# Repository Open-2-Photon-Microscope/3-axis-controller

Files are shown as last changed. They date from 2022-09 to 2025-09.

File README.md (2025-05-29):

# 3-axis-controller

A manipulator device to operate microscope stage XYZ translations. This project was specifically designed for the OpenFlexure Delta Stage.
  
## Assembly

### Assembling the Board
1. Order the (2 layer) board from a PCB manufacturer (e.g. JLCPCB) by uploading [this file](electronics/integrated_board/Fabrication%20files/integrated_board_gerbers.zip).
1. Using the [BOM](BOM.xlsx), solder together the integrated board from [electronics/integrated_board](electronics/integrated_board). The board is labeled with the locations and values of resistors, capacitors etc.
    * _Make sure to solder socket headers to the board and slot in the esp32 and pcf8575 modules rather than soldering them directly to the board. Sometimes things go wrong and they will be very hard to remove..._
    * _All parts are intended to be soldered as sitting on the top face of the board - any differences seen in the 3D view of the PCB in KiCAD should be ignored_

## Software
### Setting up MicroPython with Thonny IDE
1. Follow the tutorial on [this page](https://randomnerdtutorials.com/getting-started-thonny-micropython-python-ide-esp32-esp8266/) if you haven't already done so when assembling the board.   
### Upload the Code
1. Download the code [here](micropython/)
1. Open them all in Thonny.
    * *Connect your board to your PC via micro USB.*
1. In Thonny, in the files panel (`view > files`) navigate to the location of the code to be installed
1. Highlight all files and folders, including `lib`
1. Right click and select `Upload to /`
1. __CHECK:__ Does the file layout in the esp32 look like that on this GitHub?  

### Assembling the controller
1. Assemble the JST-XH cables mentioned in the BOM
1. For each button and flip switch, cut one crimped wire in half and solder before attaching to the JST-XH head Orientation doesn't matter.  
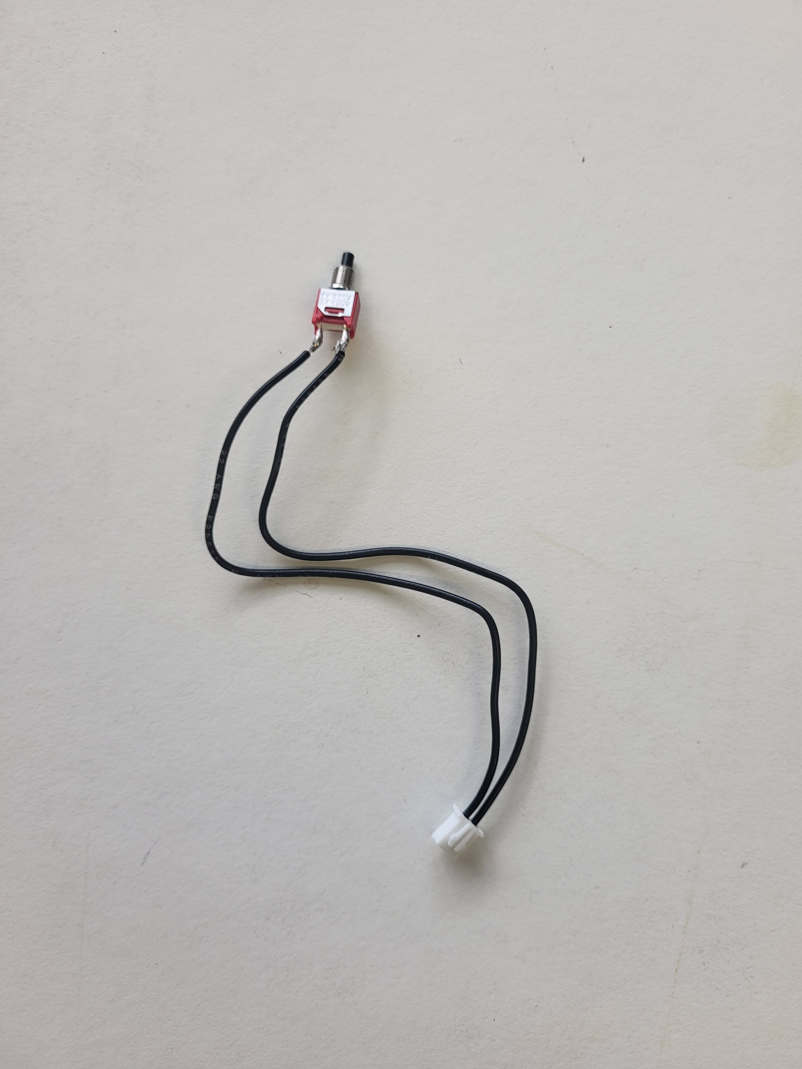
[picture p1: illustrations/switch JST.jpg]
All switches in the panel use one crimped cable cut in half
    
1. Print the [enclosure top](box%20design/enclosure_top.stl) and assemble as shown. Include the other rotary encoders and switches (not shown). The appropriate washers and nuts to screw onto the front face should be shipped with each component. Use M3x10 screws for the LCD.
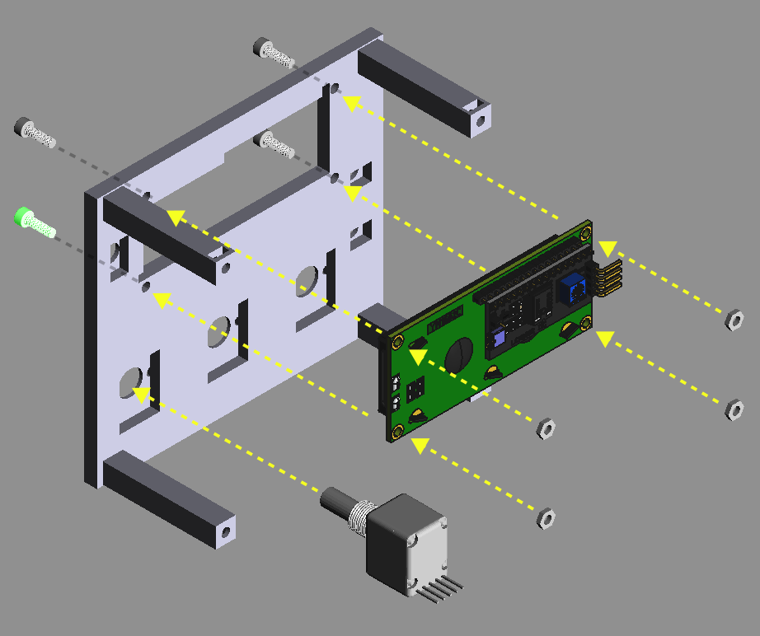
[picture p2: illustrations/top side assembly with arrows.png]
Assemble the top of the controller
      
1. Use a 4-pin JST cable to connect the LCD to the marked port. **Make sure** the GND and VCC pins are attached to the same connection on the main and LCD board.
    * _NOTE: there is a variable resistor on the back of the LCD board that adjusts the contrast, so don't screw the whole box shut until you've tested the text appears correctly_  
1. Use a 5-pin JST cable for each rotary encoder. **MAKE SURE** the GND pin connects to the pin marked with "-" on the encoder.
1. Plug in all the switches to the board to their closest port.
    * __DO NOT PLUG SWITCHES INTO THE PORTS MARKED AS 12V/GND AS IT MAY START A FIRE AND SOME FEATURES MAY NOT WORK AS INTENDED__  
1. Once you are confident the LCD is displaying text correctly when powered on, assemble the [enclosure](box%20design/enclosure.stl) as shown. Make sure to print the [feet](box%20design/enclosure_feet.stl) in some TPU for grip. Use M3x16 (or longer).  
 * _Note you should have all components wired up and screwed in at this point, not all of this is shown on the diagram._

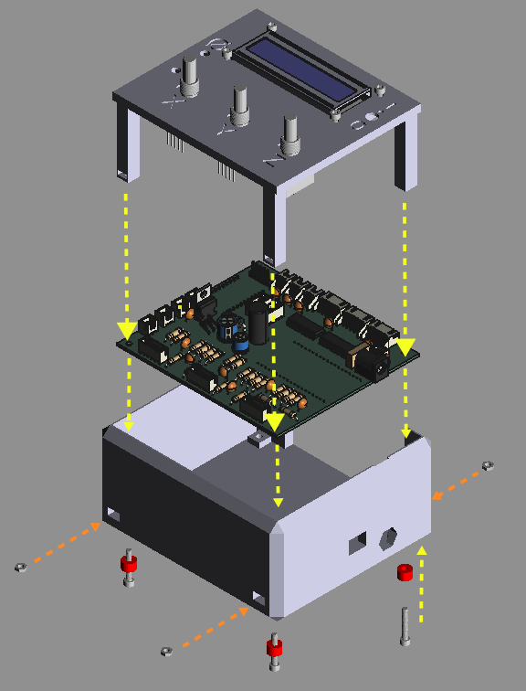
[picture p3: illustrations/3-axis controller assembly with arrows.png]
Assemble the whole box!
    
    
### Connecting to the Delta Stage
1. Split the length (2M) of ribbon cable at the ends into 3 strips of 5 wires, and 3 strips of 2 wires. You can peel away the remaining wires and discard them.
    * _Note it may be helpful for cable management not to entirely separate the 3x5 and 3x2 strips._
1. Crimp **one** end of the cable, and slot into JST XH 5 or 2 cable headers respectively.
1. Put a short length of heat-shrink tubing on each remaining end of **all** wires.
1. Next, solder the remaining 3x5 wires to straight JST HX 5 pin headers (male)
    * _Ensure the orientation of both ends of the cable is such that each lane could form a complete loop if it were plugged into itself without any twist. (i.e. each in and out pin is the same)_
1. Solder the sets of 2 wires to the footswitches - one to the middle-pin, the other to the pin towards the hinge of the lever.
    * _Ensure this configuration is such that a circuit is made (not broken) when the switch is pressed_
1. Use hot air or a soldering iron to shrink the heat-shrink tubing and cover these solder joints.
1. Use m2x8 screws to attach the switches to the [modified feet of the Delta Stage](https://github.com/Open-2-Photon-Microscope/OF-larger-delta-stage/blob/main/3D_designs/STL/feet_with_endstop.stl) and use these in place of the ones on the official models when [assembling the actuators](https://build.openflexure.org/openflexure-delta-stage/v1.2.2/pages/index_transmission/pages/assembling_the_actuators.html)
    * Make sure to use the modified models found [here](https://github.com/Open-2-Photon-Microscope/OF-larger-delta-stage/tree/main/3D_designs/STL) for the open 2-photon project  

### Installing the I2C library
#### You may need to install the `lib` portion of the I2C code another way - the above method __should__ work, so only follow these instructions if something is not behaving as expected.
1. Download [micropython-i2c-lcd-0.1.1.tar.gz](https://pypi.org/project/micropython-i2c-lcd/#files)
1. In Thonny go to `Tools > Manage Packages`
    * _make sure the esp32 is still plugged in to your computer_
1. Click the __Install from local file__ link and select the `.tar.gz` file you downloaded
1. __CHECK:__ Does the file layout in the esp32 look like that on this GitHub? You should not need to but you may have to rename the folder to ensure all the code is looking in the right place...

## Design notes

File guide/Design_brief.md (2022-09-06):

# Design brief

|Function|Constraint|Level|
| ------------- | ------------- | ------------- |
| Connect rotary encoders | Present an user interface | present rotary encoder shafts/rods : 9,8 mm holes | 
|  |  | countersink the nuts : nut thickness of 3 mm, fastening thickness 8 mm | 
|  |  | split the interface into three rotary encoders, rotary encoders dimensions : 15,9 x 21,3 mm |
|  | Contain rotary encoders and wires | rotary encoder thickness 18,5 mm |
|  |  | 35 mm depth for wires |
| Rotary encoder driver boards | Contain and fix the 3 PCBs | mounting holes center distance : 40 x 27 mm | 
|  |  | mounting holes 3,5 for M3 screws |
|  |  | board dimensions : 52 x 39 mm |
| BeeHive board | Contain and fix the Beehive board | mounting holes center distance : 76 x 67 | 
|  |  | mounting holes 3,5 for M3 screws |
|  |  | board dimensions : 85 x 76 |
|  | Power the board | Hole for 12V power supply cable and micro usb cable : 20 x 20 |
| ULN driver boards | Contain and fix the 3 PCBs | mounting holes center distance : 30,5 x 26 | 
|  | | mounting holes diameter M3 |
|  | | board dimensions : 35 x 31 |
|  | Command the motors | Hole(s) for the IN cables : 35 x 6 |

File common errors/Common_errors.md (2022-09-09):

# Common errors

## 1.  Builder

### a.  BeeHive / esp32

- Don’t power the BeeHive board with the micro usb cable only. Always use simultaneously the 12 V power supply and the 5 V micro usb power supply.
- Don’t use the analog pins called “A1”, “A2” and “A3”.
- Don’t use the pins 0 and 4 when you are connected to the computer via usb connection.

### b.  Electrical connections

If you notice that a circuit isn’t working, although each electrical connection was double checked, try to remove and solder its components to the board again.

## 2.  User

### a.  Running the code

- If the error “pin can only be input” appears, make sure that rotary encoders and motors aren’t connected to any analog pin. The analog pins are located in the “A1”, “A2” and “A3” BeeHive connectors. 



- If you’re having trouble connecting the esp32, try to close the jupyter notebook and the command prompt and start all over again.
If it persists, you can erase and flash again the esp32. 



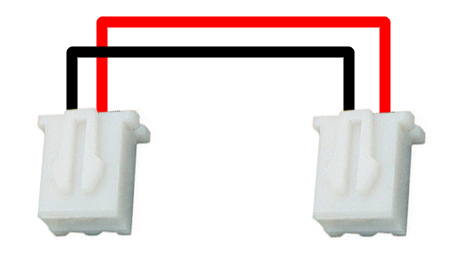
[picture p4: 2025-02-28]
illustrations/jst connect.png

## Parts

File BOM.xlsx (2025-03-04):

3-axis Controller BOM
Designator* | Name | Part Name | ppu | Qty | Cost | URL
 | I2C LCD 16x2 |  | 3.33 | 1 |  | https://www.amazon.co.uk/AZDelivery-HD44780-Display-Characters-Arduino/dp/B07JH6GHPR
Can replace? | Rotary Encoders | ENA1J-B28 L100L | 45.96 | 3 |  | https://uk.rs-online.com/web/p/motion-control-sensors/6928623?gb=s
 | Power Supply 12V |  | 8.33 | 1 |  | https://uk.rs-online.com/web/p/ac-dc-adapters/1753303?gb=s
 | Power Switch | RS 734-7154 | 3.1 | 1 |  | https://uk.rs-online.com/web/p/toggle-switches/7347154?gb=s
 | m3x10 |  | 2.78 | 4 |  | https://uk.rs-online.com/web/p/machine-screws/3180575?gb=s
 | m3x16 |  | 7.62 | 4 |  | https://uk.rs-online.com/web/p/machine-screws/3180604?searchId=9c0beb72-a0c6-4323-8691-1e1c86c068c5&gb=s
(can use brass nuts from OFDS bekow) | m3 nut |  | 6.08 | 8 |  | https://uk.rs-online.com/web/p/hex-nuts/0560293?gb=s
 | Push Switch | RS 734-6735 | 2.6 | 2 |  | https://uk.rs-online.com/web/p/push-button-switches/7346735?gb=s
Delta Stage BOM
Designator* | Name | Part Name | ppu | Qty | Cost | URL
 | PLA Filament
 | Stepper Motor (5V) | 28BBYJ-48 | 7.73 | 3 |  | https://uk.rs-online.com/web/p/power-motor-robotics-development-tools/0107010?gb=s
 | Microswitch | D2F-L-T | 1.37 | 3 |  | https://www.digikey.co.uk/en/products/detail/omron-electronics-inc-emc-div/D2F-L-T/368470
 | Ribbon Cable |  | 13.38 | 1 |  | https://uk.rs-online.com/web/p/ribbon-cable/2899896?gb=s
 | JST XH Female crimp terminal |  | 4.9 | - |  | https://uk.rs-online.com/web/p/crimp-contacts/8201529?gb=s
 | JST HX 5-way female |  | 2.35 | 3 |  | https://uk.rs-online.com/web/p/wire-housings-plugs/8201627P?gb=s
 | JST XH 5-way Straight Header |  | 1.39 | 9 |  | https://uk.rs-online.com/web/p/pcb-headers/8201560?gb=s
 | JST XH 2-way female |  | 0.5 | 8 |  | https://uk.rs-online.com/web/p/wire-housings-plugs/8201611?gb=s
(integrated board) | JST HX 2-way Right angle Header |  | 0.5 | 3 |  | https://uk.rs-online.com/web/p/pcb-headers/8201582?gb=s
(integrated board) | JST XH 5-way Right-angle Header |  | 1.63 | 3 |  | https://uk.rs-online.com/web/p/pcb-headers/8201598?gb=s
 | O-ring 30mm Bore |  | 11.42 | 3 |  | https://uk.rs-online.com/web/p/gaskets-o-rings/2587505?gb=s
 | 3x2 Magnets |  | 3.59 | 9 |  | https://www.amazon.co.uk/FINDMAG-Magnets-Fridge-Whiteboard-Hobbies/dp/B0C81JFZFH/260-8358626-8297359
 | brass m3 nut |  | 11.79 | 3 |  | https://uk.rs-online.com/web/p/hex-nuts/4832485?gb=s
 | m3 washer |  | 5.32 | 6 |  | https://uk.rs-online.com/web/p/washers/0189620?gb=s
 | m3x25 hex-head |  | 2.9 | 3 |  | https://www.ebay.co.uk/itm/394606777801?var=0&toolid=10044&customid=8db6dd95-9425-41d6-84c7-2e9b25ce04d1
 | m4x6 button head |  | 3.79 | 6 |  | https://uk.rs-online.com/web/p/machine-screws/3180632?gb=s
 | m2x8 |  | 6.07 | 6 |  | https://uk.rs-online.com/web/p/machine-screws/9141576?gb=s
Mounting the Delta Stage
 | Thorlabs PH2 1/2 post holder |  | 7.16 | 3 |  | https://www.thorlabs.com/thorproduct.cfm?partnumber=PH2#ad-image-0
 | BA1SL slotted base |  | 13.5 | 3 |  | https://www.thorlabs.com/thorproduct.cfm?partnumber=BA1SL/M#ad-image-0
 | MB2020/M - Aluminum Breadboard |  | 68.49 | 1 |  | https://www.thorlabs.com/thorproduct.cfm?partnumber=MB2020/M
 | ½”posts |  | 6.47 | 3 |  | https://www.thorlabs.com/thorproduct.cfm?partnumber=TR150/M
 | m6x20 |  | 12.84 | 3 |  | https://uk.rs-online.com/web/p/socket-screws/4733754?searchId=7e07ba86-927e-465d-a21f-89d09d501540&gb=s
Integrated Board BOM
Designator* | Name | Part Name | ppu | Qty | Cost | URL
J5, J6, J7 | JST_XH_S2B-XH-A_1x02_P2.50mm_Horizontal
P1,P10,P15 | JST_XH_B2B-XH-A_1x02_P2.50mm_Vertical
R3,R24,R15,R12,R6,R27 | 1.8k
R7 | 560R
J4, J11 | JST_XH_B2B-XH-A_1x02_P2.50mm_Vertical
R4,R23,R25,R13,R2,R1,R5,R14,R10,R26,R11,R22 | 1kΩ
J10 | PinHeader_1x05_P2.54mm_Vertical
C9,C8,C11,C1,C2,C10 | 22nF
J12, J14, J16 | JST_XH_B5B-XH-A_1x05_P2.50mm_Vertical
C3,C4 | 10µF
C12,C7,C14,C15,C13 | 33nF
J13, J15, J17 | JST_XH_S5B-XH-A_1x05_P2.50mm_Horizontal
R8 | 100K
P2, P16 | JST_XH_B4B-XH-A_1x04_P2.50mm_Vertical
U1,U2 | ULN2003
CON1 | BarrelJack_Horizontal
D1 | Schottky 5A
C5 | 680µ
R17 | 1.8K
L1 | 33µH
U3 | LM2596T-5
D2 | LED_D3.0mm
R9 | 100k
R16 | 1K
C6 | 220µ
U4 | ESP32-DEVKITC-32D
J8,J9 | PinHeader_1x10_P2.54mm_Vertical |  |  |  |  | https://uk.rs-online.com/web/p/pcb-sockets/2053168?gb=s

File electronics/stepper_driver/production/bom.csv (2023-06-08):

Designator | Footprint | Quantity | Value | LCSC Part #
J2 | JST_XH_S5B-XH-A_1x05_P2.50mm_Horizontal | 1 | Conn_01x05_Female
H1 | MountingHole_3.2mm_M3 | 1 | MountingHole
J6 | JST_XH_S5B-XH-A_1x05_P2.50mm_Horizontal | 1 | Conn_01x05_Female
U2 | DIP-16_W7.62mm_Socket_LongPads | 1 | ULN2003
C2 | C_Disc_D6.0mm_W4.4mm_P5.00mm | 1 | C_Small
U1 | DIP-16_W7.62mm_Socket_LongPads | 1 | ULN2003
J3 | JST_XH_S4B-XH-A-1_1x04_P2.50mm_Horizontal | 1 | Conn_01x04_Female
H3 | MountingHole_3.2mm_M3 | 1 | MountingHole
J4 | JST_XH_S5B-XH-A_1x05_P2.50mm_Horizontal | 1 | Conn_01x05_Female
J8 | JST_XH_S4B-XH-A-1_1x04_P2.50mm_Horizontal | 1 | Conn_01x04_Female
J1 | JST_XH_S4B-XH-A-1_1x04_P2.50mm_Horizontal | 1 | Conn_01x04_Female
J5 | JST_XH_S4B-XH-A-1_1x04_P2.50mm_Horizontal | 1 | Conn_01x04_Female
H2 | MountingHole_3.2mm_M3 | 1 | MountingHole
C1 | C_Disc_D6.0mm_W4.4mm_P5.00mm | 1 | C_Small
J9 | JST_XH_S4B-XH-A-1_1x04_P2.50mm_Horizontal | 1 | Conn_01x04_Female
H4 | MountingHole_3.2mm_M3 | 1 | MountingHole
J7 | JST_XH_S4B-XH-A-1_1x04_P2.50mm_Horizontal | 1 | Conn_01x04_Female

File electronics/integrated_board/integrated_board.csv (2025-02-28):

Id | Designator | Footprint | Quantity | Designation | Supplier and ref
1 | J6 | JST_XH_S2B-XH-A_1x02_P2.50mm_Horizontal | 1 | Endstop B
2 | P1,P10,P15 | JST_XH_B2B-XH-A_1x02_P2.50mm_Vertical | 3 | Conn_01x02
3 | R3,R24,R15,R12,R6,R27 | R_Axial_DIN0309_L9.0mm_D3.2mm_P12.70mm_Horizontal | 6 | 1.8k
4 | R7 | R_Box_L13.0mm_W4.0mm_P9.00mm | 1 | 560R
5 | H3,H2,H1,H4 | MountingHole_3.2mm_M3_DIN965 | 4 | MountingHole
6 | J4 | JST_XH_B2B-XH-A_1x02_P2.50mm_Vertical | 1 | Switch 2
7 | R4,R23,R25,R13,R2,R1,R5,R14,R10,R26,R11,R22 | R_Axial_DIN0309_L9.0mm_D3.2mm_P12.70mm_Horizontal | 12 | 1kΩ
8 | J10 | PinHeader_1x05_P2.54mm_Vertical | 1 | pcf8575 IO expander
9 | J11 | JST_XH_B2B-XH-A_1x02_P2.50mm_Vertical | 1 | Switch 1
10 | C9,C8,C11,C1,C2,C10 | C_Disc_D6.0mm_W4.4mm_P5.00mm | 6 | 22nF
11 | J12 | JST_XH_B5B-XH-A_1x05_P2.50mm_Vertical | 1 | rot_encoderX(14,27)
12 | C3,C4 | C_Disc_D6.0mm_W4.4mm_P5.00mm | 2 | 10µF
13 | C12,C7,C14,C15,C13 | C_Disc_D6.0mm_W4.4mm_P5.00mm | 5 | 33nF
14 | J13 | JST_XH_S5B-XH-A_1x05_P2.50mm_Horizontal | 1 | motor1(15,2,0,4)
15 | R8 | R_Axial_DIN0309_L9.0mm_D3.2mm_P12.70mm_Horizontal | 1 | 100K
16 | P2 | JST_XH_B4B-XH-A_1x04_P2.50mm_Vertical | 1 | LCD
17 | U1,U2 | DIP-16_W7.62mm_LongPads | 2 | ULN2003
18 | J14 | JST_XH_B5B-XH-A_1x05_P2.50mm_Vertical | 1 | rot_encoderY(25,26)
19 | J7 | JST_XH_S2B-XH-A_1x02_P2.50mm_Horizontal | 1 | Endstop C
20 | P16 | JST_XH_B4B-XH-A_1x04_P2.50mm_Vertical | 1 | UART
21 | CON1 | BarrelJack_Horizontal | 1 | BARREL_JACK
22 | D1 | D_DO-201AD_P15.24mm_Horizontal | 1 | Schottky 5A
23 | C5 | CP_Radial_D10.0mm_P2.50mm_P5.00mm | 1 | 680µ
24 | J16 | JST_XH_B5B-XH-A_1x05_P2.50mm_Vertical | 1 | rot_encoderZ(35,34)
25 | R17 | R_Axial_DIN0309_L9.0mm_D3.2mm_P12.70mm_Horizontal | 1 | 1.8K
26 | L1 | L_Radial_D10.0mm_P5.00mm_Neosid_SD12_style3 | 1 | 33µH
27 | U3 | TO-220-5_P3.4x3.7mm_StaggerOdd_Lead3.8mm_Vertical | 1 | LM2596T-5
28 | J17 | JST_XH_S5B-XH-A_1x05_P2.50mm_Horizontal | 1 | motor3 (19,21,22,23)
29 | D2 | LED_D3.0mm | 1 | LED
30 | R9 | R_Axial_DIN0309_L9.0mm_D3.2mm_P12.70mm_Horizontal | 1 | 100k
31 | J15 | JST_XH_S5B-XH-A_1x05_P2.50mm_Horizontal | 1 | motor2 (16,17,5,18)
32 | R16 | R_Axial_DIN0309_L9.0mm_D3.2mm_P12.70mm_Horizontal | 1 | 1K
33 | C6 | CP_Radial_D8.0mm_P3.80mm | 1 | 220µ
34 | J5 | JST_XH_S2B-XH-A_1x02_P2.50mm_Horizontal | 1 | Endstop A
35 | U4 | MODULE_ESP32-DEVKITC-32D | 1 | ESP32-DEVKITC-32D
36 | J8,J9 | PinHeader_1x10_P2.54mm_Vertical | 2 | Conn_01x16

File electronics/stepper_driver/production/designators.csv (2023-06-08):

J2:1
H1:1
J6:1
U2:1
C2:1
U1:1
J3:1
H3:1
J4:1
J8:1
J1:1
J5:1
H2:1
C1:1
J9:1
H4:1
J7:1

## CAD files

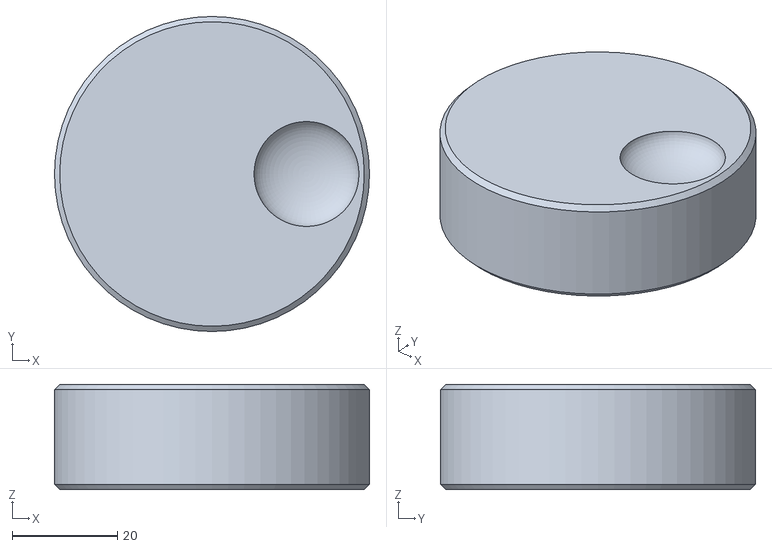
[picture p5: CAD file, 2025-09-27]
box design/wheel.stl
60.0 x 60.0 x 20.0

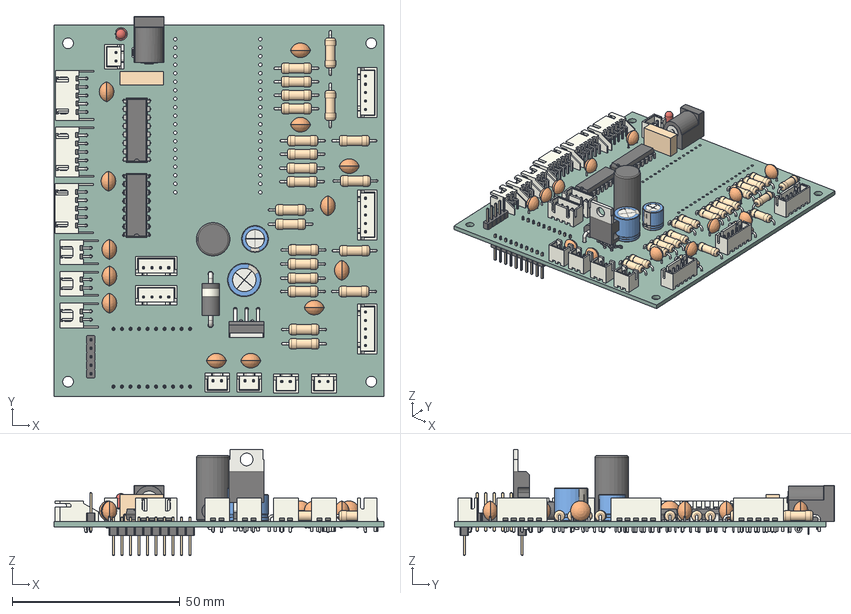
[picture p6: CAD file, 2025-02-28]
electronics/integrated_board/integrated_board.step
98.5 x 113.5 x 31.7 mm
JST_S2B_XH_A x 3
JST_B2B_XH_A x 5
R_Axial_DIN0309_L90mm_D32mm_P1270mm_Horizontal x 22
R_Box_L130mm_W40mm_P900mm
PinHeader_1x05_P254mm_Vertical
C_Disc_D60mm_W44mm_P500mm x 13
JST_B5B_XH_A x 3
JST_S5B_XH_A x 3
JST_B4B_XH_A x 2
DIP-16_W7.62mm x 2
BarrelJack_Horizontal
D_DO-201AD_P15.24mm_Horizontal
CP_Radial_D100mm_P250mm_P500mm
L_Radial_D10.0mm_P5.00mm_Neosid_SD12_style3
TO_220_5_Pentawatt_Multiwatt_5_Vertical_StaggeredType1
LED_D3.0mm
CP_Radial_D80mm_P380mm
PinHeader_1x10_P254mm_Vertical x 2
integrated_board_PCB

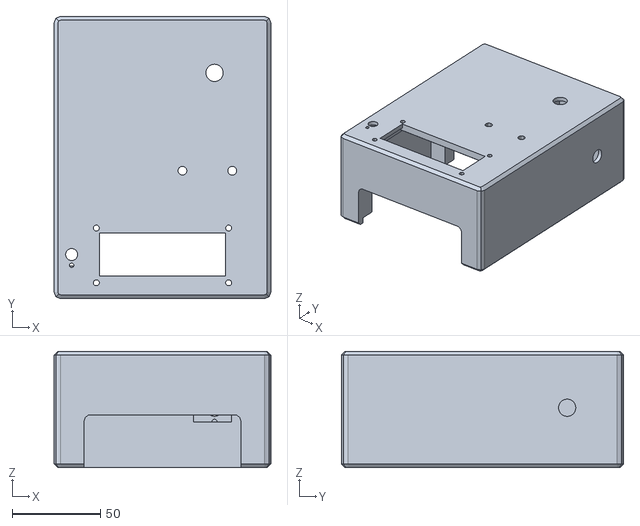
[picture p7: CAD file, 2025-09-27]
box design/3-axis-controller.stl
123.0 x 160.0 x 66.0

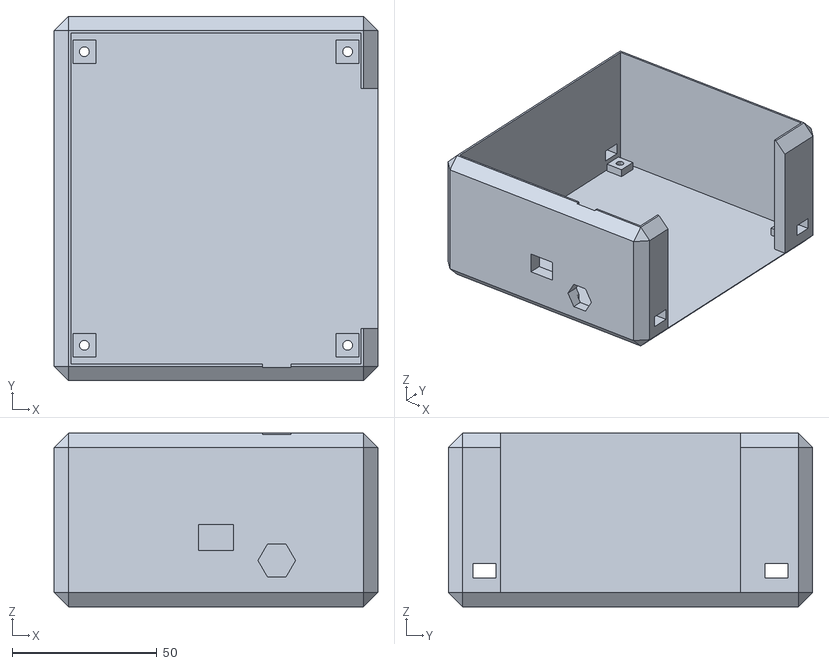
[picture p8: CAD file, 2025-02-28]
box design/enclosure.stl
112.0 x 126.0 x 60.0

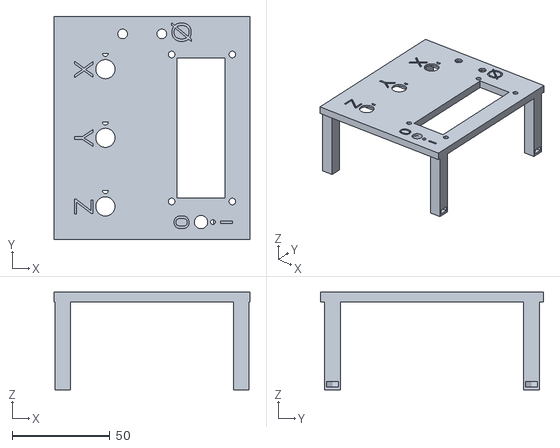
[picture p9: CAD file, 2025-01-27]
box design/enclosure_top.stl
100.0 x 114.0 x 50.0

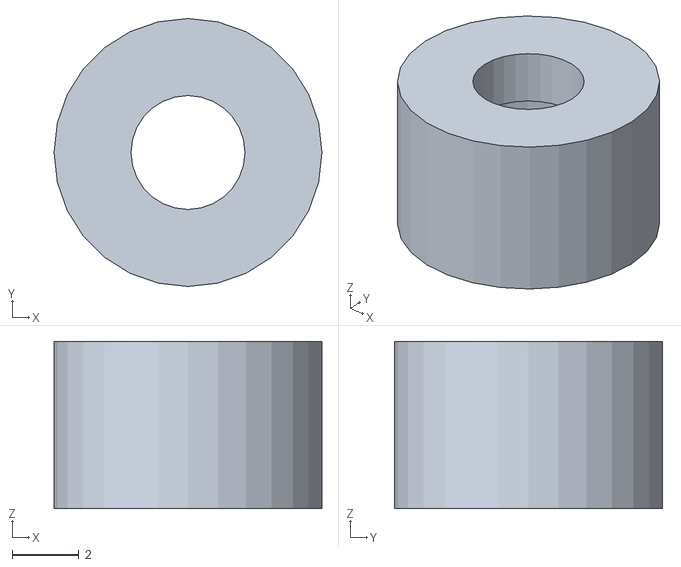
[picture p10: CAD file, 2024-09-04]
box design/enclosure_feet.stl
8.00 x 8.00 x 5.00

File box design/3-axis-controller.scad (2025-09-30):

//3-axis controller
use <wheel.scad>
use <enclosure.scad>
use <fillets_and_rounds.scad>

space = 30;

module dial(){
    union(){
translate([-1.22,0,-10])ena1j();
translate([0,0,2.05])color("red",0.3)wheel();}}

module test_box(){
difference(){
    translate([-15,-15,-15])add_rounds(R=4,fn=6)cube(47);
    translate([-16,-16,-16])cube(40);
    translate([0,0,space])rotate([0,0,90])dial();
    translate([0,space,0])rotate([-90,0,0])dial();
    translate([space,0,0])rotate([90,-90,90])dial();}}

//test_box();

module dials(){
color("red",0.3){translate([0,0,space])rotate([0,0,90])dial();
translate([0,space,0])rotate([-90,0,0])dial();
translate([space,0,0])rotate([90,-90,90])dial();}}

//translate([30,30,30])dials();

module Xboard(){
    $fn=6;
    translate([3.6,5.2])cylinder(d=3.3,h=10);
    translate([42,53.5,0])cylinder(d=3.3,h=10);
    %cube([48,60,1]);
}//end Xboard



module box(x=113,y=150,z=56,w=10){
    difference(){
        translate([-w/2,-w/2,0])add_rounds(R=4,fn=7)cube([x+w,y+w,z+w]);
        translate([0,0,-1])cube([x,y,z+1]);
        translate([x+w/2-32,y+w/2-32,z+w-32])dials();
        translate([12,-w,-5])add_rounds(R=4,axis="y")cube([x-24,w*2,35]);
        translate([-w,20,-5])add_rounds(R=4,axis="x")cube([w*2,42,30]);
        translate([x*0.6,y*0.45,z+2])push_switch();
        translate([x*0.85,y*0.45,z+2])push_switch();
        translate([x/2,20,z+7])rotate([0,0,-90])lcd();
        translate([5,20,z+3])rotate([0,0,-90])pwr_switch();
        translate([x+w-60,y-49,z-5])rotate([0,0,90])Xboard();
    }//end difference
    difference(){
    for(xi=[0:101:102]){
            for(yi=[0:90.5:91]){
                translate([xi,yi,4])cube([12,10,z-4]);}}
    translate([0,1,0])board();}
    %translate([x+w/2-32,y+w/2-32,z+w-32])dials();
}//end box

box();

module board(h=10,d=3.3){
        %linear_extrude(5)polygon([[0,0],[0,98.5],[111,98.5],[110,0]]);
        linear_extrude(h)translate([5.5,4.2])for(x=[0:101:102]){
            for(y=[0:90.5:91]){
                translate([x,y])circle(d=d,$fn=6);
            }}//end for
}//end board

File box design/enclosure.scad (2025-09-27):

module base(x, y, h=5, slot=true, hr=0.25, outer=true, hole_diam=3.4){
    // x and y refer to screw hole positions
    translate([-1*x/2,y/2,0])screw_post(h, slot=slot, hole_ratio=hr,outer=outer,hole_diam=hole_diam);
    translate([-1*x/2,-1*y/2,0])screw_post(h, slot=slot, hole_ratio=hr,outer=outer,hole_diam=hole_diam);
    rotate([0,0,180]){
        translate([-1*x/2,y/2,0])screw_post(h, slot=slot, hole_ratio=hr,outer=outer,hole_diam=hole_diam);
        translate([-1*x/2,-1*y/2,0])screw_post(h, slot=slot, hole_ratio=hr,outer=outer,hole_diam=hole_diam);
    }//end rotate
    
}// end module base

//base(91,101); // board x=91 y=101

//base(91,101,h=45,hr=0.5);


//base(75,32); // lcd

module screw_post(height, nut_h=2.8,slot=true, hole_ratio=0.25,outer=true,hole_diam=3.4){
    translate([0,0,height/2])difference(){
        if(outer==true){
            // shell
            cube([8,8,height],center=true);}
        // cutouts
        union(){
            // center hole
            translate([0,0,height/2]){rotate([180,0,0])cylinder(d=hole_diam, h= height*hole_ratio, $fn=18);}
            
            if(slot==true){
            // nut
            translate([0,0,height/2-3])cylinder(d=6.95, h= nut_h, center=true,$fn=6);
            // side exit
            translate([-5,0,height/2-3])cube([10,6,nut_h],center=true);
            // overhang trick
            translate([0,0,height/2-1.6])cube([3.4,6,0.3],center=true);}//end if
        }
        
    }// end difference
}// end module screw_post

//screw_post(20,hole_ratio=0.25);


module ena1j(){ // model of the rotary encoder
    cube([21.5,16,18.5],center=true);
    translate([21.5/2-9.53,0,18.5/2-1])cylinder(d=9.8,h=7.35,$fn=28);
    translate([21.5/2-9.53,8,18.5/2]){difference(){
        cylinder(h=1.7,d=3,$fn=18);
        translate([0,3.5/2,0])cube(3.5,center=true);
    }//end difference
    }//end translate
}//end ena1j

//ena1j();

module lcd(){
    // screen
    translate([0,0,4-9])cube([24.5,71.5,18],center=true);
    
    // space for soldered pins
    translate([(24.5+6.6)/2,71.5/2-42/2,-13/2])cube([6.6,42,14],center=true);
    
    // space for part of backlight
    translate([0,(71.5+4.6)/-2,-13/2])cube([24.5,4.6,13],center=true);
    
    //board
    translate([0,0,-7])cube([38,82,10],center=true);
    
    //screw holes
    translate([16,75/2,0])cylinder(d=3.4,h=15, center=true, $fn=18);
    translate([-15,75/2,0])cylinder(d=3.4,h=15, center=true, $fn=18);
    translate([16,-75/2,0])cylinder(d=3.4,h=15, center=true, $fn=18);
    translate([-15 ,-75/2,0])cylinder(d=3.4,h=15, center=true, $fn=18);
}// end lcd



module pwr_switch(){
    cube([13, 7,8.9],center=true);
    translate([0,0,8.9/2-1])cylinder(d=6.8,h=9.9,$fn=25);
    translate([6.1,0,8.9/2-1])cylinder(d=2.5,h=4,$fn=18);
}// end module pwr_switch

//pwr_switch();

module push_switch(){
    cube([6.9,8.4,8.4],center=true);
    translate([0,0,3.2])cylinder(d=5,h=6.6,$fn=18);
}//end module push_switch

//push_switch();

module feet(d, screw_d, head_d, h){
    $fn = 28;
    difference(){
        cylinder(d=d, h=h);
        cylinder(d = screw_d, h=h);
        cylinder(d=head_d, h=h*2/3);
    }//end difference
}// end module feet


module fancy_box(x,y,z,thickness){
    hull(){
        cube([x+thickness,y,z],center=true);
        cube([x,y+thickness,z],center=true);
        cube([x,y,z+thickness],center=true);
    }//end hull
}//end fancy_box


module top_enclosure(x, y, z, h){
    enj_depth = -8;
    enj_x = -30;
    enj_y = 35;
    difference(){
    union(){
        translate([0,0,z/2])difference(){
        cube([x, y, z], center=true);
        union(){
            translate([25,0,0.75])lcd();
            
            translate([5,-5,0]){ // ena1j encoders
            translate([enj_x,enj_y,enj_depth])ena1j();
            translate([enj_x,0,enj_depth])ena1j();
            translate([enj_x,-1*enj_y,enj_depth])ena1j();
            }// end translate
            
            translate([25,-48,-3.5])pwr_switch();
            
            translate([5,0,0]){ // push switches
            translate([0,48,-3.2])push_switch();
            translate([-20,48,-3.2])push_switch();
            }// end translate
        }//end union
        }//end difference
        rotate([180,0,0])base(91,101.5,h,hr=0.5);
    }
    translate([0,0,5-1])top_markings();
    }//end difference
}//end module top_lvl


module top_markings(){
    assert(ord("\u0000") == 32);
    rotate([0,0,-90]){
        linear_extrude(1.5){
        translate([-30,-35,0])text("X",halign="center",valign="center");
        translate([5,-35,0])text("Y",halign="center",valign="center");
        translate([40,-35,0])text("Z",halign="center",valign="center");
        
        translate([-49,15,0])text("Ø",halign="center",valign="center");
        //translate([-49,-15,0])text("\u2714",halign="center",valign="center");
        
        translate([48,38,0]){scale([1,0.6,1])text("l",halign="center",valign="center");}
        translate([48,15,0]){scale([1,1,1])text("o",halign="center",valign="center");}
    }//end linear_extrude
    }//end rotate
}//end top_markings


module outer_enclosure(x=102, y=116, z=50){
    inner_dims = [100.3,114.3,60];
    thickness=10;
    difference(){
        union(){
    difference(){
        translate([0,0,-z/2+5-thickness/2])fancy_box(x,y,z,10);
        translate([0,0,-20])cube(inner_dims,center=true);
    }//end difference
    //stands
    translate([0,0,-z-thickness/2+3.5])base(91,101.5,5, slot=false);
    } // end union
    //screw holes
    translate([0,0,-z-thickness/2])base(91,101.5,20, hr=1, slot=false,outer=false);
    //nut slots for outer access (just in case)
    translate([0,0,-z-thickness/2+10])base(106,101,5, slot=false, hr=-1);
    //usb hole
    translate([0,-y/2,-31])cube([12,15,9],center=true);
    //power port
    translate([21,-y/2,-39]){rotate([90,0,0])cylinder(d=13,h=15,$fn=6,center=true);}
    //power port slot
    translate([21,-inner_dims[1]/2,5-z/2])cube([10,2.5,inner_dims[2]],center=true);
    // motor output
    translate([inner_dims[0]/2,-3.5,5-z/2])cube([20,83,inner_dims[2]],center=true);
}// end difference
}//end module outer_enclosure

%top_enclosure(100,114,5,45);
outer_enclosure();
//feet(8, 3.4, 5.6, 5); // print in TPU or something soft for grip

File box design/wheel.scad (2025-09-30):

// Control wheels for 3-axis controller
use <fillets_and_rounds.scad>

module shaft(id=6.6,od=10,slot_w=1,ih=18,oh=5,sl=10){
    $fn=30;
    cylinder(d=id,h=ih);
    translate([0,0,-1])cylinder(d=od,h=oh+1);
    translate([0,0,ih/2])add_rounds(axis="z",R=0.4)cube([slot_w,od,ih],center=true);
}//end shaft

module c_wheel(d=40,h=20,ddimple=15,ddepth=10,fillet=2,fn=40){
    $fn=fn;
    translate([0,0,h/2])difference(){
        hull(){
            cylinder(d=d-fillet,h=h,center=true);
            cylinder(d=d,h=h-fillet,center=true);
        }//end hull
        translate([d/2-ddimple/2-fillet,0,h/2])scale([1,1,ddepth/ddimple])sphere(d=ddimple);
    }//end difference
}//end c_wheel

module wheel(d=60,h=20,ddimple=20,ddepth=10,fillet=2,fn=60,
id=6.4,od=15.5,slot_w=1,ih=18,oh=5,sl=10){
difference(){
c_wheel(d=d,h=h,ddimple=ddimple,ddepth=ddepth,fillet=fillet,fn=fn);
shaft(id=id,od=od,slot_w=slot_w,ih=ih,oh=oh,sl=sl);
}}

wheel();

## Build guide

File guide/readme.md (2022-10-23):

<details>
<summary>Summary</summary>

<details>
<summary>Builder guide</summary>

* Bill of materials
    * Delta stage
    * Electronics
    * Box
* Bill of tools and skills
    * CAD
    * FFF 3D printer
    * Soldering bench
    * Electronic bench
    * Programming

</details>

<details>
<summary>Developer guide</summary>

* How has the project been developed ?
    * The box CAD
    * Electronics
    * Code
    * Kinematics
* Current state of development
    * Tasks currently worked on
    * Open task priorities
* Documentation/references

</details> 

</details>

#  Builder guide

## 1.  Bill of materials

In this part we will focus on what components were used and why they were used. Please find the [BOM](https://github.com/Open-2-Photon-Microscope/3-axis-controller/tree/main/BOM) as table format on the repository.

### a.  Delta stage

The [OpenFlexure Delta Stage](https://openflexure.org/projects/deltastage/) is an acknowledged open source device initially designed as a microscope stage. Papers about it were published, which means data such as drift, resolution and stability are available. The stage 3-axis translations are controlled via three 28BYJ-48 -- 5V unipolar stepper motors. This is why the code was specifically developed for coil sequences activation of this kind of motors. Openflexure's program is aimed for Arduino, but in order to broaden our target audience, we wrote a Python program, which runs an esp32 microcontroller.

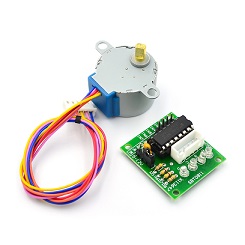
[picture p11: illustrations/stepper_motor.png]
28BYJ-48 stepper motor


### b.  Electronics
- To connect the Delta Stage to our manipulator, we are using a [BeeHive](https://github.com/amchagas/BeeHive) board. It's a platform using esp32 as microcontroller, which requires a 12 V power input and presents many 5 V outputs to connect devices. Beware about the common connection mistakes you can make using the BeeHive (check [Common errors](https://github.com/Open-2-Photon-Microscope/3-axis-controller/blob/main/common%20errors/Common_errors.md) doc part 1. a.).
- The rotary encoders are connected to the BeeHive board through a PCB custom made for this project. It contains pull-up resistors and filter capacitors, which are recommended in the component data sheet for proper operation. There's also a bridge divider reducing the encoder channel signal voltage from 5 V to 3 V for the esp32 power supply.
- Here is a connection scheme from one rotary encoder to one motor.

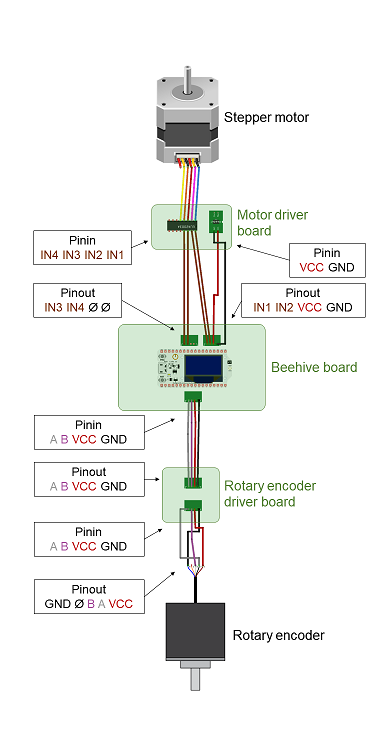
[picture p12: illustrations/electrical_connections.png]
Electrical connection scheme


### c.  Box

The electrical connections above-mentioned are contained in a box. This box is also the concrete outcome users are going to interact with to control the delta stage. It can be 3D printed (FFF) with PLA, and requires about 350 g of material. To assemble the PCBs in it, you will need :
- 56 x M3 nuts
- 28 x M3 screws, 6 mm below head length, Ø5 mm head diameter

## 2.  Bill of tools and skills

### a.  CAD

To update the design, you will need **FreeCAD** software. It's better if you're familiar with it. More details about the way the CAD was made is written in the following [3. a.](https://github.com/Open-2-Photon-Microscope/3-axis-controller/blob/main/documentation/Developer_guide.md#a--the-box-cad). If you need to modify the rotary encoder board, you'll need to use **KiCad**.

### b.  FFF 3D printer

We sliced the part via **PrusaSlicer**, setting the layer height to 0,20 mm. It is made out of four independent parts : front, frame, below and rear. You can download the four stl files from the GitHub repo. The only part that requires a bit of support is the cap. An infill of 15% is enough, and could even be lightly reduced.

### c.  Soldering bench

In order to assemble the BeeHive board, the custom made PCB and some electrical connections such as the rotary encoder ones, you will need to deal with soldering.

### d.  Electronic bench

In case you need to do some functionality tests, you will need some basic electronic tools, such as an oscilloscope, or a multimeter for instance.

### e.  Programming

To upgrade the code, or understand its structure, you'll need some knowledge in **Python**. We used the **Jupyter Notebook IDE** to develop and run the code on the manipulator.

# Developer guide

## 3.  How has the project been developed ?

### a.  The box CAD

It is parametrized, so if you want to customise it, you can open the source file in FreeCAD and directly change the wanted parameter in the Spreadsheet. Here is a table which identifies the different parameter spreadsheets :

| Table name | Parameter | Explanation |
| ------------- | ------------- | ------------- |
| Spreadsheet.front | length | box length without taking into account the 2 sides thickness |
|  | height  | box height without taking into account the top and below sides thickness |
|  | fastening thickness | thread length |
|  | thickness | pocket depth minus slack |
|  | notch length | - |
|  | slack | assembly slack for pocket depth |
|  | frame thickness | - |
|  | nut thickness | rotary encoder nut thickness |
|  | centre distance | distance between to rotary encoder rod center |
|  | encoder width | - |
|  | rod diameter | rotary encoder rod diameter |
|  | nut edge | rotary encoder nut edge |
|  | hole | rotary encoder rod hole |
|  | encoder height | - |
|  | encoder height below shaft | - |
|  | part thickness | front part thickness. Equals to fastening thickness + thickness + slack. |
| Spreadsheet.below | below side thickness | - |
|  | screw head diameter | assembly screw head diameter |
|  | screw head thickness | assembly screw head thickness |
|  | screw length | assembly screw length |
|  | hole diameter | mounting hole diameter |
|  | PCB center distance 1 | biggest distance between 2 PCB (rotary encoder board) mounting hole centers |
|  | PCB center distance 2 | smallest distance between 2 PCB (rotary encoder board) mounting hole centers |
| | PCB dimension 1 | biggest PCB (rotary encoder board) dimension |
|  | PCB dimension 2 | smallest PCB (rotary encoder board) dimension |
|  | BeeHive center distance 1 | biggest distance between 2 BeeHive board mounting hole centers |
|  | BeeHive center distance 2 | smallest distance between 2 BeeHive board mounting hole centers |
|  | BeeHive dimension 1 | biggest BeeHive board dimension |
|  | BeeHive dimension 2 | smallest BeeHive board dimension |
|  | PCB gap | distance between 2 boards |
|  | rotary encoder thickness | - |
|  | RE wire connection depth | volume dedicated to rotary encoder connection wires |
|  | box depth | inside box depth. Equals to rotary encoder thickness + RE wire connection depth + PCB dimension 1 + BeeHive dimension 2 + ULN board dimension2 + 3 * PCB gap |
|  | mounting hole diameter | - |
|  | below part thickness | - |
|| assembly gap | gap dedicated to counter 3D printed imprecision and allow by hand assembly |
|  | motor cables hole height | rectangle side dimension for motor cables |
|  | motor cables hole length | rectangle side dimension for motor cables |
|  | power supply hole | square side dimension for power supply cables |

If you are curious about a specific box feature, please find its [design brief](https://github.com/Open-2-Photon-Microscope/3-axis-controller/blob/main/developer%20guide/Design_brief.md) on the repository.

## b.  Electronics

To allow a proper operation of each rotary encoder, and reduce channel voltage to 3V for esp32 power supply, we had to design a custom made board. We used KiCad to draw the schematics and then design the board. The schematics and the board source files are available in the Github repo. If you only aime to manufacture it again, please find the gerber file in the same place.

## c.  Code

The code has been developed on a Jupyter Notebook. It has been implemented in several modules :

- Pin assignment

You can find here two functions: one that assigns channels A and B of each rotary encoder to pins and another that assigns motors to pins.

- Motor functions

    - The first function defines the motor sequence depending on the command : clockwise, counter clockwise or freeze.
    - The second one runs the required amount of steps. If the required number is negative, let's say "-n", it will run "n" counter clockwise sequences.
    - The third one assigns the required motor rotation combination to each translation axis. For example, if the Y-axis rotary encoder sends a clockwise command, motors a and b are going to run -4 steps and motor c 8 steps. This conversion from cartesian to delta movement is explained in d. Kinematics.

- Rotary encoder function

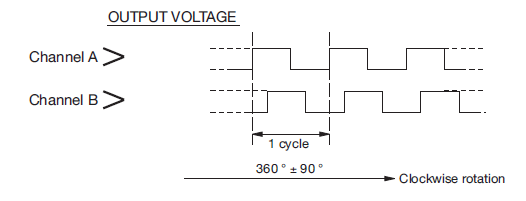
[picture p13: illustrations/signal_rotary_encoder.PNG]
Output voltage signal rotary encoder


This function translates the rotary encoder signal into motor rotations. Channels A and B have square signals, with high (=1) and low (=0) output values. However the signals are slightly delayed one another. The first channel to reach the high output value indicates if the encoder is turned either clockwise or counterclockwise. In order to know which signal is ahead, the code implements two data: the channel value and the channel state. The channel state is the current output value minus the previous one. When this state is equal to 1, it means that the output has changed from high to low. So, if channel A state is 1 and channel B output value is 0, then channel A is the first one to reach high output. This means that the rotary encoder is being turned clockwise. On the contrary, if channel B state is 1 and channel A output value is 0, the rotary encoder is being turned anticlockwise.

- Program

The program is an open loop. Its first step is to assign the rotary encoder channels pins and the motor pins as well. In the open loop, each rotary encoder is assigned to a translation axis, and runs motor rotation if the appropriate output voltage is detected.

### d.  Kinematics

The 28byj-48 stepper motor has four coils that can be activated by sequences. Depending on the sequence pattern, the motor will turn clockwise or counterclockwise. Here is the clockwise sequence pattern: \[1,0,0,0\], \[0,1,0,0\], \[0,0,1,0\], \[0,0,0,1\]. Each sequence activates one motor step. So, every complete sequence pattern activates four motor steps. The original motor step is 0,18°. So the motor has to do 2038 steps to complete a rotation.

To reach the sub micron step size, you would have to upgrade the program. We have been focusing on steps (sub micron steps would be called "microsteps"). In order to translate in one axis translation, the Delta Stage requires a specific motor combination. According to the matrix below, one positive unit in the x direction requires -cos30 (= - 0,87) motor a step and one 0,87 motor b step. In order to command a decimal step value you would require PWM. As it lowers the device stability and consumes a lot of energy, we wanted to first test the device with whole steps.

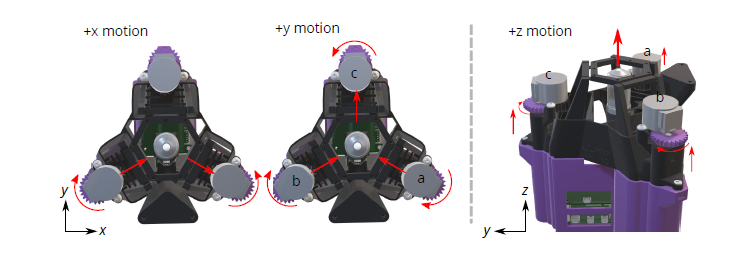
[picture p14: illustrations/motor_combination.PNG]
Motor combination for cartesian translations Motor combination for cartesian translations, from *Multimodal microscopy imaging with the OpenFlexure Delta Stage*


Matrix Matrix, from *Multimodal microscopy imaging with the OpenFlexure Delta Stage*

The littlest multiple that would allow a complete whole number step value combination is 8. This way, the new motor step is 1,44°, so 250 steps would complete a whole motor shaft rotation.

|  | 8 steps |
| ------------- | ------------- |
| 1 | 8 steps |
| | 1,44° |
| 0,5 = cos60 | 4 steps |
|| 0,72° |
| 0,87 = cos30 | 6,96 ≈ 7 steps |
|| 1,25° |

The new change of basis can now be written:

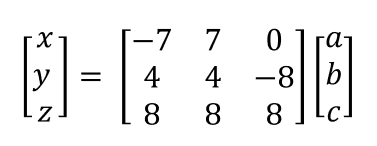
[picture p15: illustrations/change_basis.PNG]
Change of basis
 

## 4.  Current state of development

### a.  tasks currently worked on

Have a look at the [github projects](https://github.com/Open-2-Photon-Microscope/3-axis-controller/projects?type=classic), to check the current state of development.

### b.  open task priorities

- [Acceptance tests](https://github.com/Open-2-Photon-Microscope/3-axis-controller/projects/6#card-85028599):
    -  check how well it moves in X,Y,Z (as the code we are implementing converts delta stage movement to cartesian)
    -  see what is the minimum amount we can move
    -  see how fast things are moving
    -  see how stable the system is without moving (drifts over 30min/hour? or even longer)

- Programming
    -  Refine the open loop program. OpenFlexure uses a specific algorithm to overcome open loop backlashes.
    -  The user has to be able to command the stage to translate to a specific location.
    -  Allow the device to do microstepping. The minimal step size has to be sub-micron.

## 5.  Documentation/references

### a.  Delta Stage
- James P. Sharkey, Darryl C. W. Foo, Alexandre Kabla, et al. «A one-piece 3D printed flexure translation stage for open-source microscopy.» *Review of Scientific Instruments*, 2016. https://doi.org/10.1063/1.4941068
- McDermott, S., Ayazi, F., Collins, J., Knapper, J., Stirling, J., Bowman, R., & Cicuta, P. «Multimodal microscopy imaging with the OpenFlexure Delta Stage.» *Optics Express*, 2022. https://doi.org/10.1364/OE.450211

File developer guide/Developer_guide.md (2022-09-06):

# Developer guide

## 1.  Bill of materials

In this part we will focus on what components were used and why they were used. Please find the [BOM](https://github.com/Open-2-Photon-Microscope/3-axis-controller/tree/main/BOM) as table format on the repository.

### a.  Delta stage

The [OpenFlexure Delta Stage](https://openflexure.org/projects/deltastage/) is an acknowledged open source device initially designed as a microscope stage. Papers about it were published, which means data such as drift, resolution and stability are available. The stage 3-axis translations are controlled via three 28BYJ-48 -- 5V unipolar stepper motors. This is why the code was specifically developed for coil sequences activation of this kind of motors. Openflexure's program is aimed for Arduino, but in order to broaden our target audience, we wrote a Python program, which runs an esp32 microcontroller.

28BYJ-48 stepper motor

### b.  Electronics
- To connect the Delta Stage to our manipulator, we are using a [BeeHive](https://github.com/amchagas/BeeHive) board. It's a platform using esp32 as microcontroller, which requires a 12 V power input and presents many 5 V outputs to connect devices. Beware about the common connection mistakes you can make using the BeeHive (check [Common errors](https://github.com/Open-2-Photon-Microscope/3-axis-controller/blob/main/common%20errors/Common_errors.md) doc part 1. a.).
- The rotary encoders are connected to the BeeHive board through a PCB custom made for this project. It contains pull-up resistors and filter capacitors, which are recommended in the component data sheet for proper operation. There's also a bridge divider reducing the encoder channel signal voltage from 5 V to 3 V for the esp32 power supply.
- Here is a connection scheme from one rotary encoder to one motor.

Electrical connection scheme

### c.  Box

The electrical connections above-mentioned are contained in a box. This box is also the concrete outcome users are going to interact with to control the delta stage. It can be 3D printed (FFF) with PLA, and requires about 350 g of material. To assemble the PCBs in it, you will need :
- x 56 M3 nuts
- x 28 M3 screws, 6 mm below head length, Ø5 mm head diameter

## 2.  Bill of tools and skills

### a.  CAD

To update the design, you will need **FreeCAD** software. It's better if you're familiar with it. More details about the way the CAD was made is written in the following [3. a.](https://github.com/Open-2-Photon-Microscope/3-axis-controller/blob/main/documentation/Developer_guide.md#a--the-box-cad). If you need to modify the rotary encoder board, you'll need to use **KiCad**.

### b.  FFF 3D printer

We sliced the part via **PrusaSlicer**, setting the layer height to 0,20 mm. It is made out of three independant parts : front, below, cap and frame. You can download the four stl files from the Github repo. The only part that requires a bit of support is the cap. An infill of 15% is enough, and could even be lightly reduced.

### c.  Soldering bench

In order to assemble the BeeHive board, the custom made PCB and some electrical connections such as the rotary encoder ones, you will need to deal with soldering.

### d.  Electronic bench

In case you need to do some functionality tests, you will need some basic electronic tools, such as an oscilloscope, or a multimeter for instance.

### e.  Programming

To upgrade the code, or understand its structure, you'll need some knowledge in **Python**. We used the **Jupyter Notebook IDE** to develop and run the code on the manipulator.

## 3.  How has the project been developed ?

### a.  The box CAD

It is parametrized, so if you want to customise it, you can open the source file in FreeCAD and directly change the wanted parameter in the Spreadsheet. Here is a table which identifies the different parameter spreadsheets :

| Table name | Parameter | Explanation |
| ------------- | ------------- | ------------- |
| Spreadsheet.front | length | box length without taking into account the 2 sides thickness |
|  | height  | box height without taking into account the top and below sides thickness |
|  | fastening thickness | thread length |
|  | thickness | pocket depth minus slack |
|  | notch length | - |
|  | slack | assembly slack for pocket depth |
|  | frame thickness | - |
|  | nut thickness | rotary encoder nut thickness |
|  | centre distance | distance between to rotary encoder rod center |
|  | encoder width | - |
|  | rod diameter | rotary encoder rod diameter |
|  | nut edge | rotary encoder nut edge |
|  | hole | rotary encoder rod hole |
|  | encoder height | - |
|  | encoder height below shaft | - |
|  | part thickness | front part thickness. Equals to fastening thickness + thickness + slack. |
| Spreadsheet.below | below side thickness | - |
|  | screw head diameter | assembly screw head diameter |
|  | screw head thickness | assembly screw head thickness |
|  | screw length | assembly screw length |
|  | hole diameter | mounting hole diameter |
|  | PCB center distance 1 | biggest distance between 2 PCB (rotary encoder board) mounting hole centers |
|  | PCB center distance 2 | smallest distance between 2 PCB (rotary encoder board) mounting hole centers |
| | PCB dimension 1 | biggest PCB (rotary encoder board) dimension |
|  | PCB dimension 2 | smallest PCB (rotary encoder board) dimension |
|  | BeeHive center distance 1 | biggest distance between 2 BeeHive board mounting hole centers |
|  | BeeHive center distance 2 | smallest distance between 2 BeeHive board mounting hole centers |
|  | BeeHive dimension 1 | biggest BeeHive board dimension |
|  | BeeHive dimension 2 | smallest BeeHive board dimension |
|  | PCB gap | distance between 2 boards |
|  | rotary encoder thickness | - |
|  | RE wire connection depth | volume dedicated to rotary encoder connection wires |
|  | box depth | inside box depth. Equals to rotary encoder thickness + RE wire connection depth + PCB dimension 1 + BeeHive dimension 2 + ULN board dimension2 + 3 * PCB gap |
|  | mounting hole diameter | - |
|  | below part thickness | - |
|| assembly gap | gap dedicated to counter 3D printed imprecision and allow by hand assembly |
|  | motor cables hole height | rectangle side dimension for motor cables |
|  | motor cables hole length | rectangle side dimension for motor cables |
|  | power supply hole | square side dimension for power supply cables |

If you are curious about a specific box feature, please find its [design brief](https://github.com/Open-2-Photon-Microscope/3-axis-controller/blob/main/developer%20guide/Design_brief.md) on the repository.

## b.  Electronics

To allow a proper operation of each rotary encoder, and reduce channel voltage to 3V for esp32 power supply, we had to design a custom made board. We used KiCad to draw the schematics and then design the board. The schematics and the board source files are available in the Github repo. If you only aime to manufacture it again, please find the gerber file in the same place.

## c.  Code

The code has been developed on a Jupyter Notebook. It has been implemented in several modules :

- Pin assignment

You can find here two functions: one that assigns channels A and B of each rotary encoder to pins and another that assigns motors to pins.

- Motor functions

    - The first function defines the motor sequence depending on the command : clockwise, counter clockwise or freeze.
    - The second one runs the required amount of steps. If the required number is negative, let's say "-n", it will run "n" counter clockwise sequences.
    - The third one assigns the required motor rotation combination to each translation axis. For example, if the Y-axis rotary encoder sends a clockwise command, motors a and b are going to run -4 steps and motor c 8 steps. This conversion from cartesian to delta movement is explained in d. Kinematics.

- Rotary encoder function

Output voltage signal rotary encoder

This function translates the rotary encoder signal into motor rotations. Channels A and B have square signals, with high (=1) and low (=0) output values. However the signals are slightly delayed one another. The first channel to reach the high output value indicates if the encoder is turned either clockwise or counterclockwise. In order to know which signal is ahead, the code implements two data: the channel value and the channel state. The channel state is the current output value minus the previous one. When this state is equal to 1, it means that the output has changed from high to low. So, if channel A state is 1 and channel B output value is 0, then channel A is the first one to reach high output. This means that the rotary encoder is being turned clockwise. On the contrary, if channel B state is 1 and channel A output value is 0, the rotary encoder is being turned anticlockwise.

- Program

The program is an open loop. Its first step is to assign the rotary encoder channels pins and the motor pins as well. In the open loop, each rotary encoder is assigned to a translation axis, and runs motor rotation if the appropriate output voltage is detected.

### d.  Kinematics

The 28byj-48 stepper motor has four coils that can be activated by sequences. Depending on the sequence pattern, the motor will turn clockwise or counterclockwise. Here is the clockwise sequence pattern: \[1,0,0,0\], \[0,1,0,0\], \[0,0,1,0\], \[0,0,0,1\]. Each sequence activates one motor step. So, every complete sequence pattern activates four motor steps. The original motor step is 0,18°. So the motor has to do 2038 steps to complete a rotation.

To reach the sub micron step size, you would have to upgrade the program. We have been focusing on steps (sub micron steps would be called "microsteps"). In order to translate in one axis translation, the Delta Stage requires a specific motor combination. According to the matrix below, one positive unit in the x direction requires -cos30 (= - 0,87) motor a step and one 0,87 motor b step. In order to command a decimal step value you would require PWM. As it lowers the device stability and consumes a lot of energy, we wanted to first test the device with whole steps.

Motor combination for cartesian translations

Matrix

The littlest multiple that would allow a complete whole number step value combination is 8. This way, the new motor step is 1,44°, so 250 steps would complete a whole motor shaft rotation.

|  | 8 steps |
| ------------- | ------------- |
| 1 | 8 steps |
| | 1,44° |
| 0,5 = cos60 | 4 steps |
|| 0,72° |
| 0,87 = cos30 | 6,96 ≈ 7 steps |
|| 1,25° |

## 4.  Current state of development

### a.  tasks currently worked on

Have a look at the [github projects](https://github.com/Open-2-Photon-Microscope/3-axis-controller/projects?type=classic), to check the current state of development.

### b.  open task priorities

- [Acceptance tests](https://github.com/Open-2-Photon-Microscope/3-axis-controller/projects/6#card-85028599):
    -  check how well it moves in X,Y,Z (as the code we are implementing converts delta stage movement to cartesian)
    -  see what is the minimum amount we can move
    -  see how fast things are moving
    -  see how stable the system is without moving (drifts over 30min/hour? or even longer)

- Programming
    -  Refine the open loop program. OpenFlexure uses a specific algorithm to overcome open loop backlashes.
    -  The user has to be able to command the stage to translate to a specific location.
    -  Allow the device to do microstepping. The minimal step size has to be sub-micron.

## 5.  Documentation/references

### a.  Delta Stage
- James P. Sharkey, Darryl C. W. Foo, Alexandre Kabla, et al. «A one-piece 3D printed flexure translation stage for open-source microscopy.» *Review of Scientific Instruments*, 2016. https://doi.org/10.1063/1.4941068
- McDermott, S., Ayazi, F., Collins, J., Knapper, J., Stirling, J., Bowman, R., & Cicuta, P. «Multimodal microscopy imaging with the OpenFlexure Delta Stage.» *Optics Express*, 2022. https://doi.org/10.1364/OE.450211

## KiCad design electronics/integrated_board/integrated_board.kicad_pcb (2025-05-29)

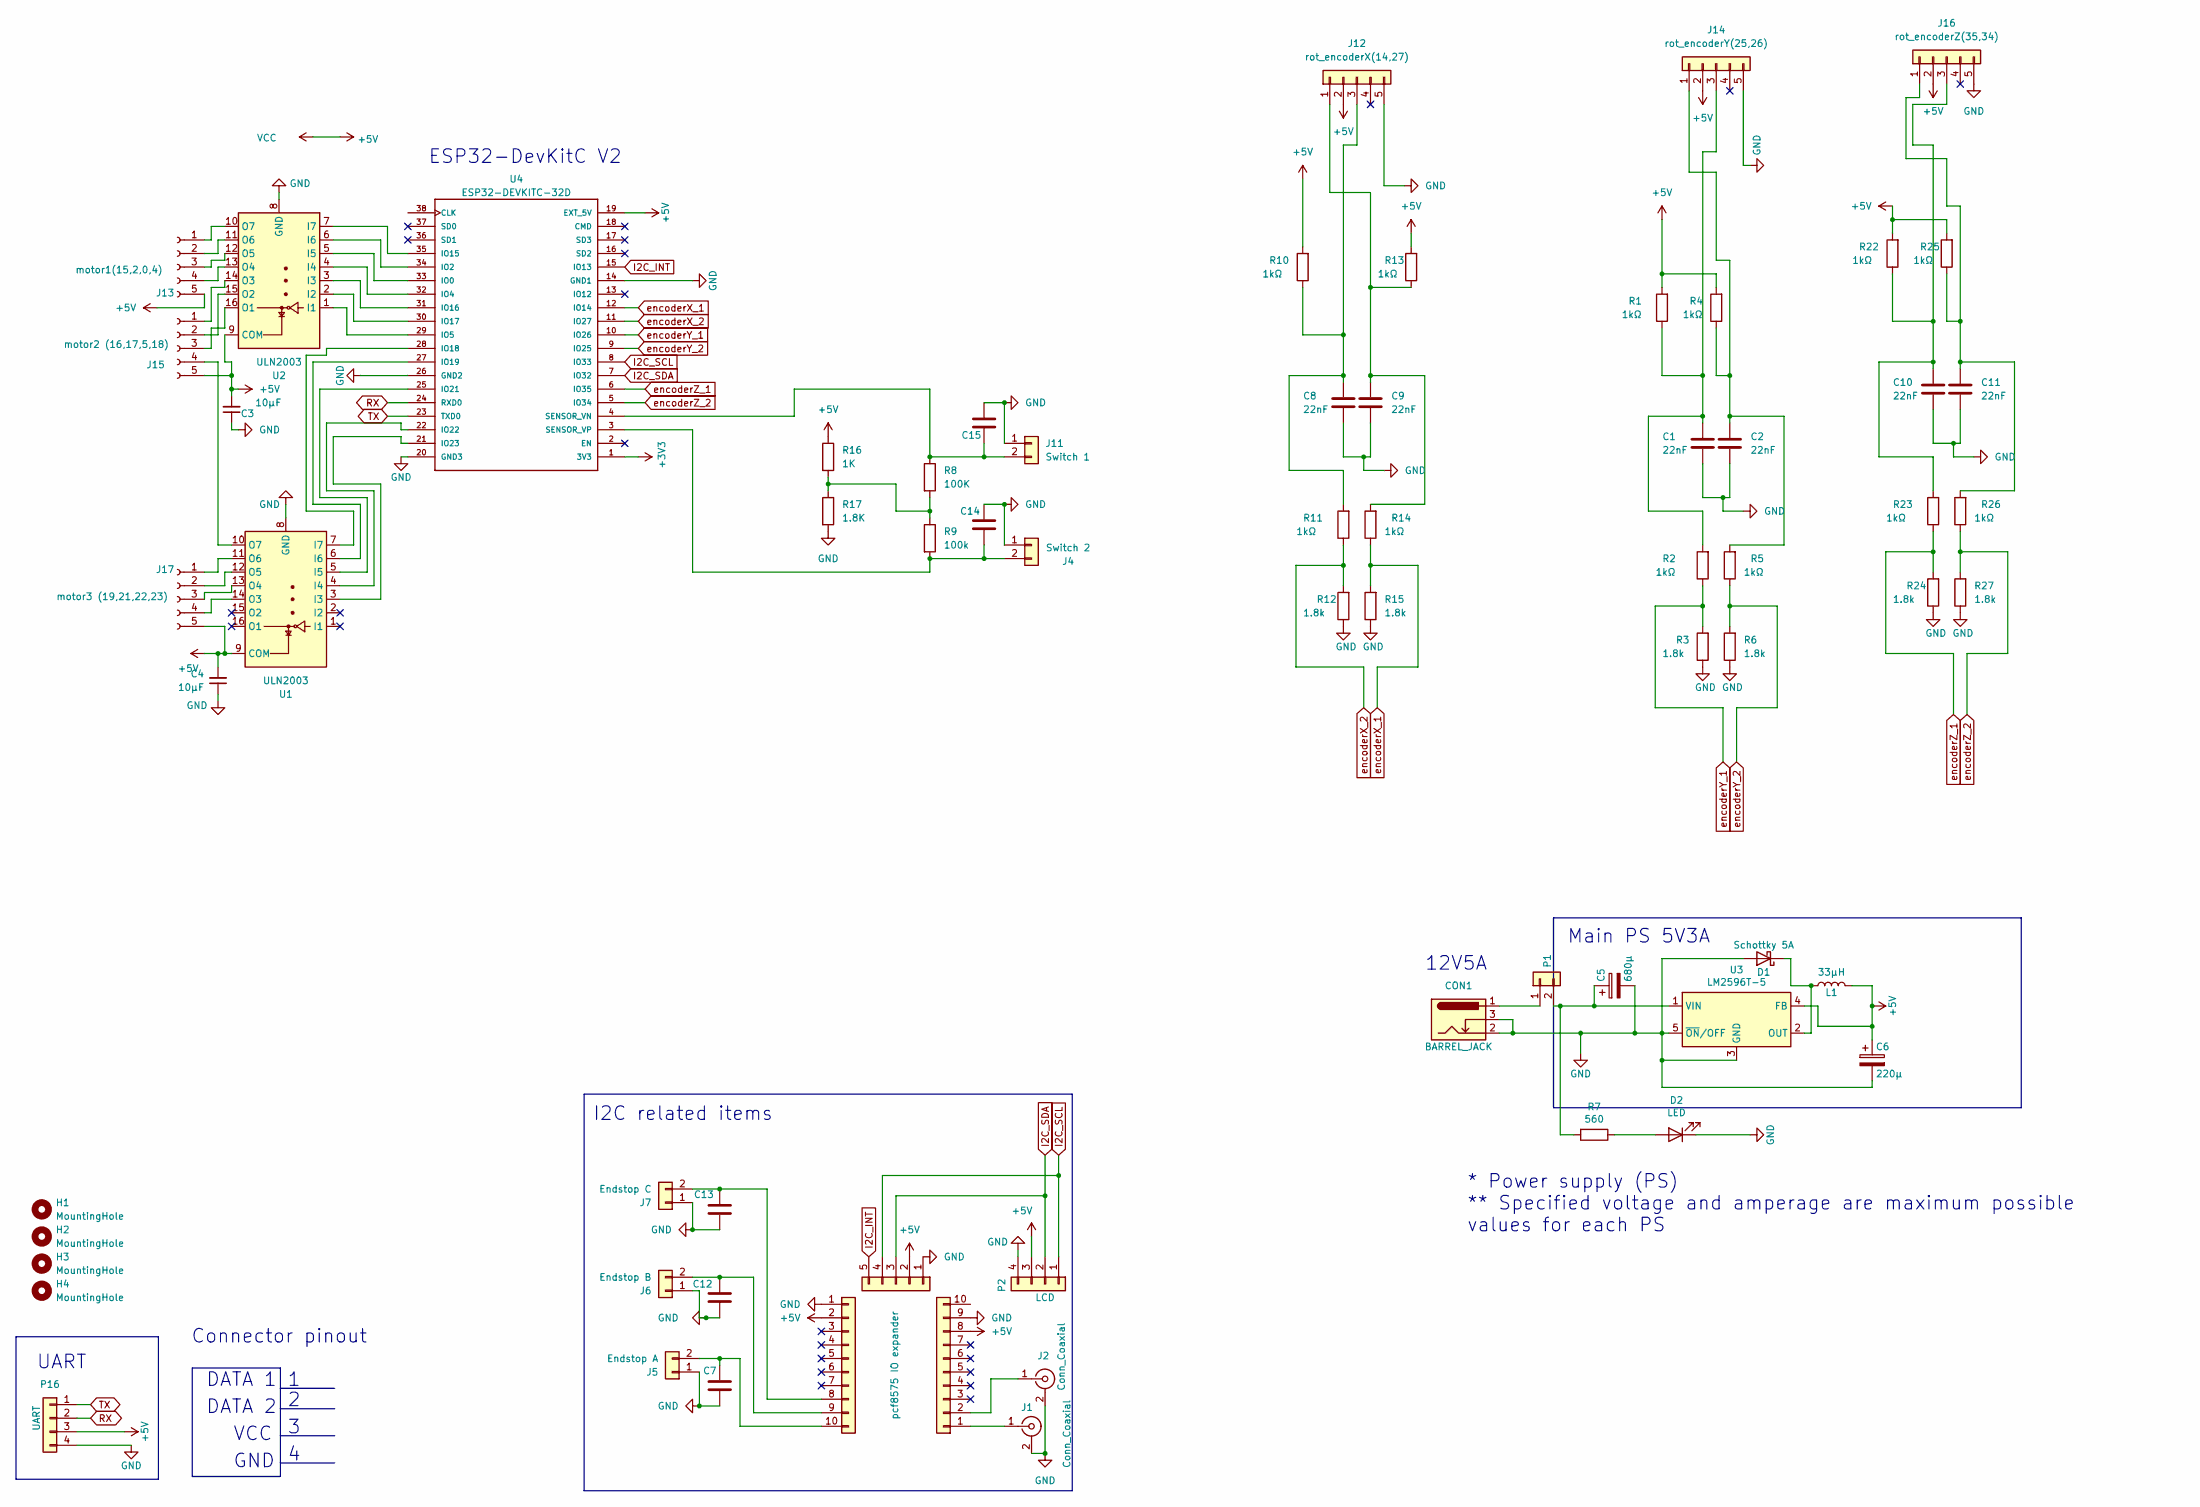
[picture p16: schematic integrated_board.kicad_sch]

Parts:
C1, C2, C8, C9, C10, C11: 22nF; C_Disc_D6.0mm_W4.4mm_P5.00mm
C3, C4: 10µF; C_Disc_D6.0mm_W4.4mm_P5.00mm
C5: 680µ; CP_Radial_D10.0mm_P2.50mm_P5.00mm
C6: 220µ; CP_Radial_D8.0mm_P3.80mm
C7, C12, C13, C14, C15: 33nF; C_Disc_D6.0mm_W4.4mm_P5.00mm
CON1: BARREL_JACK; BarrelJack_Horizontal
D1: Schottky 5A; D_DO-201AD_P15.24mm_Horizontal
D2: LED; LED_D3.0mm
H1, H2, H3, H4: MountingHole; MountingHole_3.2mm_M3_DIN965
J1, J2: Conn_Coaxial; BNC_Amphenol_B6252HB-NPP3G-50_Horizontal
J4: Switch 2; JST_XH_B2B-XH-A_1x02_P2.50mm_Vertical
J5: Endstop A; JST_XH_S2B-XH-A_1x02_P2.50mm_Horizontal
J6: Endstop B; JST_XH_S2B-XH-A_1x02_P2.50mm_Horizontal
J7: Endstop C; JST_XH_S2B-XH-A_1x02_P2.50mm_Horizontal
J8, J9: Conn_01x16; PinHeader_1x10_P2.54mm_Vertical
J10: pcf8575 IO expander; PinHeader_1x05_P2.54mm_Vertical
J11: Switch 1; JST_XH_B2B-XH-A_1x02_P2.50mm_Vertical
J12: rot_encoderX(14,27); JST_XH_B5B-XH-A_1x05_P2.50mm_Vertical
J13: motor1(15,2,0,4); JST_XH_S5B-XH-A_1x05_P2.50mm_Horizontal
J14: rot_encoderY(25,26); JST_XH_B5B-XH-A_1x05_P2.50mm_Vertical
J15: motor2 (16,17,5,18); JST_XH_S5B-XH-A_1x05_P2.50mm_Horizontal
J16: rot_encoderZ(35,34); JST_XH_B5B-XH-A_1x05_P2.50mm_Vertical
J17: motor3 (19,21,22,23); JST_XH_S5B-XH-A_1x05_P2.50mm_Horizontal
L1: 33µH; L_Radial_D10.0mm_P5.00mm_Neosid_SD12_style3
P1: Conn_01x02; JST_XH_B2B-XH-A_1x02_P2.50mm_Vertical
P2: LCD; JST_XH_B4B-XH-A_1x04_P2.50mm_Vertical
P16: UART; JST_XH_B4B-XH-A_1x04_P2.50mm_Vertical
R1, R2, R4, R5, R10, R11, R13, R14, R22, R23, R25, R26: 1kΩ; R_Axial_DIN0309_L9.0mm_D3.2mm_P12.70mm_Horizontal
R3, R6, R12, R15, R24, R27: 1.8k; R_Axial_DIN0309_L9.0mm_D3.2mm_P12.70mm_Horizontal
R7: 560; R_Box_L13.0mm_W4.0mm_P9.00mm
R8: 100K; R_Axial_DIN0309_L9.0mm_D3.2mm_P12.70mm_Horizontal
R9: 100k; R_Axial_DIN0309_L9.0mm_D3.2mm_P12.70mm_Horizontal
R16: 1K; R_Axial_DIN0309_L9.0mm_D3.2mm_P12.70mm_Horizontal
R17: 1.8K; R_Axial_DIN0309_L9.0mm_D3.2mm_P12.70mm_Horizontal
U1, U2: ULN2003; DIP-16_W7.62mm_LongPads
U3: LM2596T-5; TO-220-5_P3.4x3.7mm_StaggerOdd_Lead3.8mm_Vertical
U4: ESP32-DEVKITC-32D; MODULE_ESP32-DEVKITC-32D

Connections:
+3V3: U4.1 (3V3)
+5V: C3.2, C4.2, C6.1, J8.8, J9.2, J10.2, J12.2, J13.5, J14.2, J15.5, J16.2, J17.5, L1.2, P2.3, P16.3, R1.2, R4.2, R10.2, R13.2, R16.1, R22.2, R25.2, U1.9 (COM), U2.9 (COM), U3.4 (FB), U4.19 (EXT_5V)
GND: C1.1, C2.1, C3.1, C4.1, C5.2, C6.2, C7.1, C8.1, C9.1, C10.1, C11.1, C12.1, C13.1, C14.1, C15.1, CON1.2, CON1.3, D1.2 (A), D2.1 (K), J1.2 (Ext), J2.2 (Ext), J4.1, J5.1, J6.1, J7.1, J8.9, J9.1, J10.1, J11.1, J12.5, J14.5, J16.5, P2.4, P16.4, R3.1, R6.1, R12.1, R15.1, R17.2, R24.1, R27.1, U1.8 (GND), U2.8 (GND), U3.3 (GND), U3.5 (~ON/OFF), U4.14 (GND1), U4.20 (GND3), U4.26 (GND2)
I2C_INT: J10.5, U4.15 (IO13)
I2C_SCL: J10.4, P2.1, U4.8 (IO33)
I2C_SDA: J10.3, P2.2, U4.7 (IO32)
unnamed: D1.1 (K), L1.1, U3.2 (OUT)
unnamed: D2.2 (A), R7.1
unnamed: C14.2, J4.2, R9.2, U4.3 (SENSOR_VP)
unnamed: C7.2, J5.2, J9.10
unnamed: C12.2, J6.2, J9.9
unnamed: C13.2, J7.2, J9.8
unnamed: C15.2, J11.2, R8.1, U4.4 (SENSOR_VN)
unnamed: C9.2, J12.1, R13.1, R14.2
unnamed: C8.2, J12.3, R10.1, R11.2
unnamed: J13.1, U2.10 (O7)
unnamed: J13.2, U2.11 (O6)
unnamed: J13.3, U2.12 (O5)
unnamed: J13.4, U2.13 (O4)
unnamed: C2.2, J14.1, R4.1, R5.2
unnamed: C1.2, J14.3, R1.1, R2.2
unnamed: J15.1, U2.14 (O3)
unnamed: J15.2, U2.15 (O2)
unnamed: J15.3, U2.16 (O1)
unnamed: J15.4, U1.10 (O7)
unnamed: C11.2, J16.1, R25.1, R26.2
unnamed: C10.2, J16.3, R22.1, R23.2
unnamed: J17.1, U1.11 (O6)
unnamed: J17.2, U1.12 (O5)
unnamed: J17.3, U1.13 (O4)
unnamed: J17.4, U1.14 (O3)
unnamed: CON1.1, P1.1
unnamed: C5.1, P1.2, R7.2, U3.1 (VIN)
unnamed: R8.2, R9.1, R16.2, R17.1
unnamed: U1.3 (I3), U4.21 (IO23)
unnamed: U1.4 (I4), U4.22 (IO22)
unnamed: U1.5 (I5), U4.25 (IO21)
unnamed: U1.6 (I6), U4.27 (IO19)
unnamed: U1.7 (I7), U4.28 (IO18)
unnamed: U2.1 (I1), U4.29 (IO5)
unnamed: U2.2 (I2), U4.30 (IO17)
unnamed: U2.3 (I3), U4.31 (IO16)
unnamed: U2.4 (I4), U4.32 (IO4)
unnamed: U2.5 (I5), U4.33 (IO0)
unnamed: U2.6 (I6), U4.34 (IO2)
unnamed: U2.7 (I7), U4.35 (IO15)
RX: P16.2, U4.24 (RXD0)
TX: P16.1, U4.23 (TXD0)
encoderX_1: R14.1, R15.2, U4.12 (IO14)
encoderX_2: R11.1, R12.2, U4.11 (IO27)
encoderY_1: R2.1, R3.2, U4.10 (IO26)
encoderY_2: R5.1, R6.2, U4.9 (IO25)
encoderZ_1: R23.1, R24.2, U4.6 (IO35)
encoderZ_2: R26.1, R27.2, U4.5 (IO34)

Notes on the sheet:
I2C related items
DATA 2
UART
Main PS 5V3A
12V5A
Connector pinout
DATA 1
GND
* Power supply (PS) ** Specified voltage and amperage are maximum possible values for each PS
VCC
ESP32-DevKitC V2

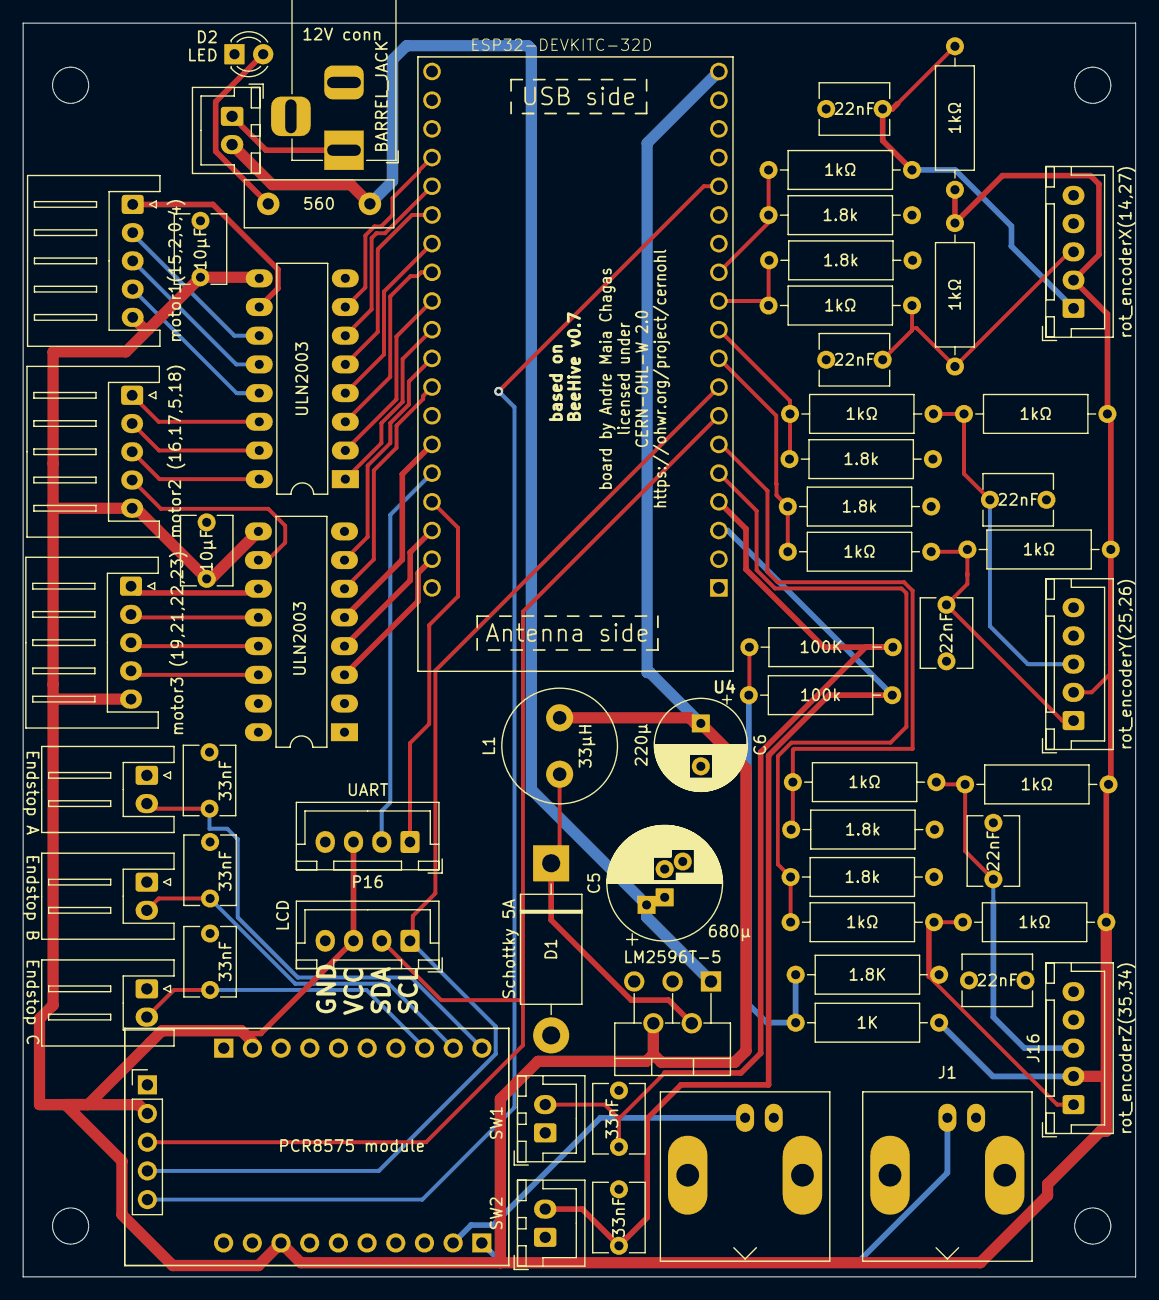
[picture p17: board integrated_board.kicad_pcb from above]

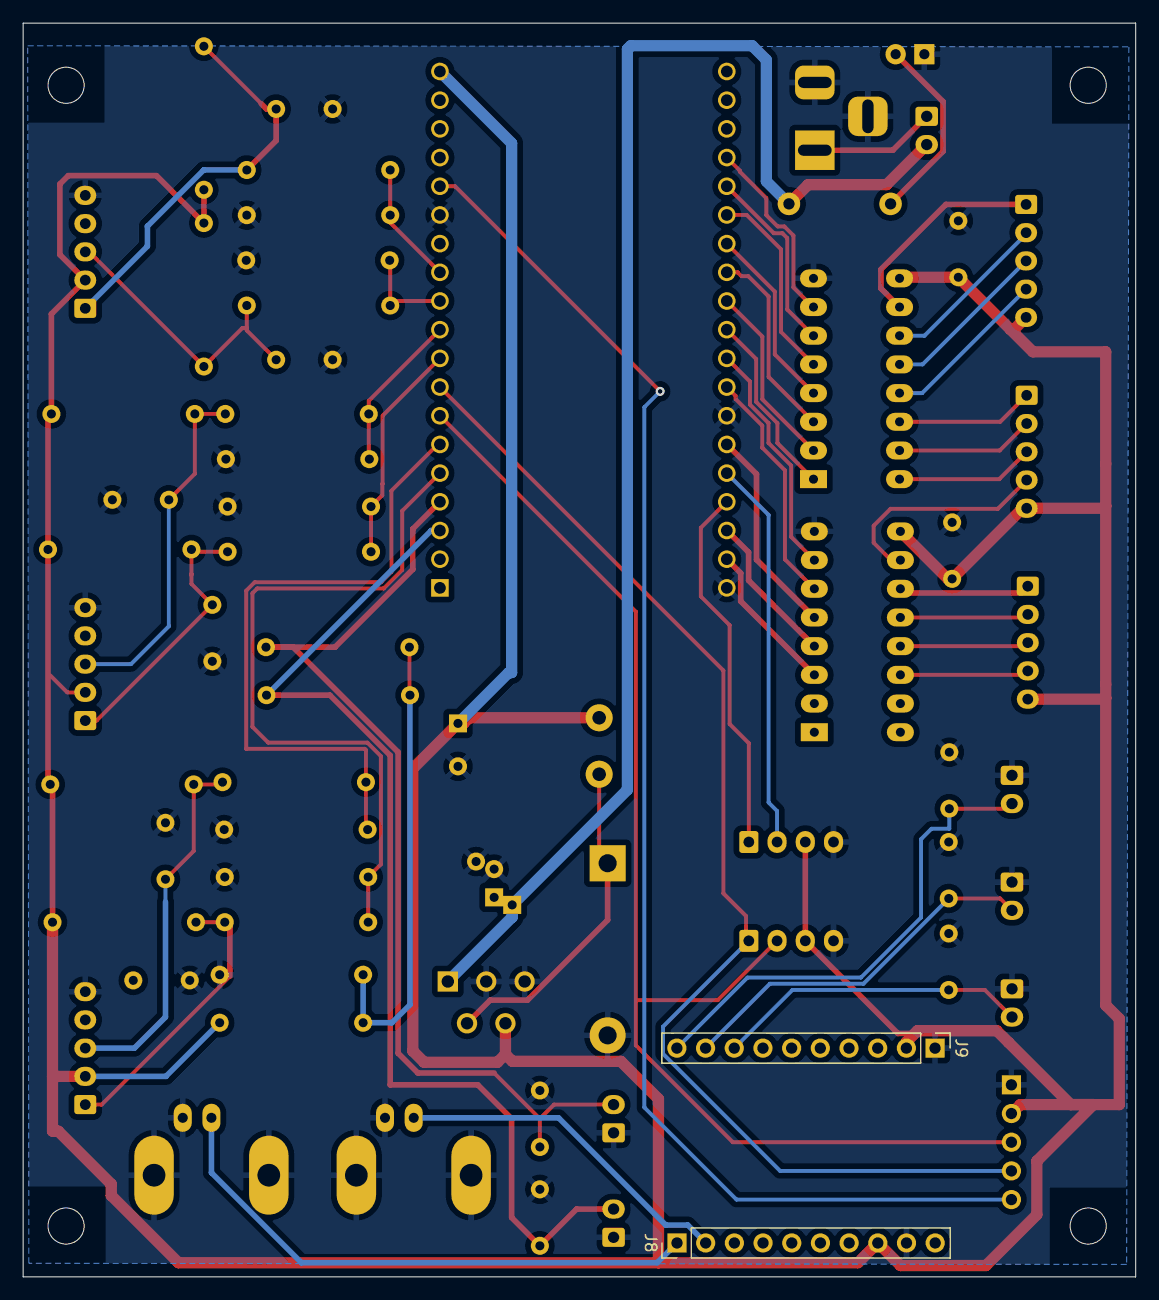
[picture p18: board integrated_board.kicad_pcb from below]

Board: 2 copper layers, 98.5 x 111.0 mm, 69 parts (2 on the bottom side), 53 nets.

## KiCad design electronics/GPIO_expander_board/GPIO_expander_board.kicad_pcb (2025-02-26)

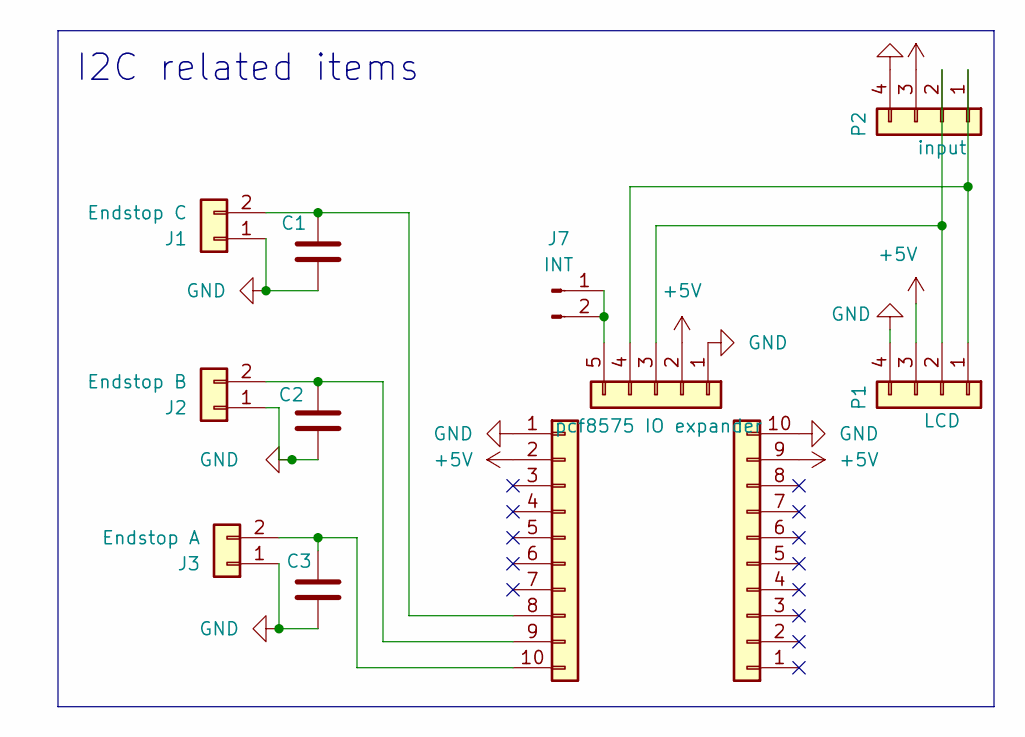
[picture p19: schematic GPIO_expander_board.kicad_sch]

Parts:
C1, C2, C3: 33nF; C_Disc_D6.0mm_W4.4mm_P5.00mm
J1: Endstop C; JST_XH_S2B-XH-A_1x02_P2.50mm_Horizontal
J2: Endstop B; JST_XH_S2B-XH-A_1x02_P2.50mm_Horizontal
J3: Endstop A; JST_XH_S2B-XH-A_1x02_P2.50mm_Horizontal
J4, J6: Conn_01x16; PinHeader_1x10_P2.54mm_Vertical
J5: pcf8575 IO expander; PinHeader_1x05_P2.54mm_Vertical
J7: INT; PinHeader_1x02_P2.54mm_Vertical
P1: LCD; JST_XH_B4B-XH-A_1x04_P2.50mm_Vertical
P2: input; JST_XH_B4B-XH-A_1x04_P2.50mm_Vertical

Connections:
+5V: J4.2, J5.2, J6.9, P1.3, P2.3
GND: C1.1, C2.1, C3.1, J1.1, J2.1, J3.1, J4.1, J5.1, J6.10, P1.4, P2.4
unnamed: C1.2, J1.2, J4.8
unnamed: C2.2, J2.2, J4.9
unnamed: C3.2, J3.2, J4.10
unnamed: J5.3, P1.2, P2.2
unnamed: J5.4, P1.1, P2.1
unnamed: J5.5, J7.1, J7.2

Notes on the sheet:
I2C related items

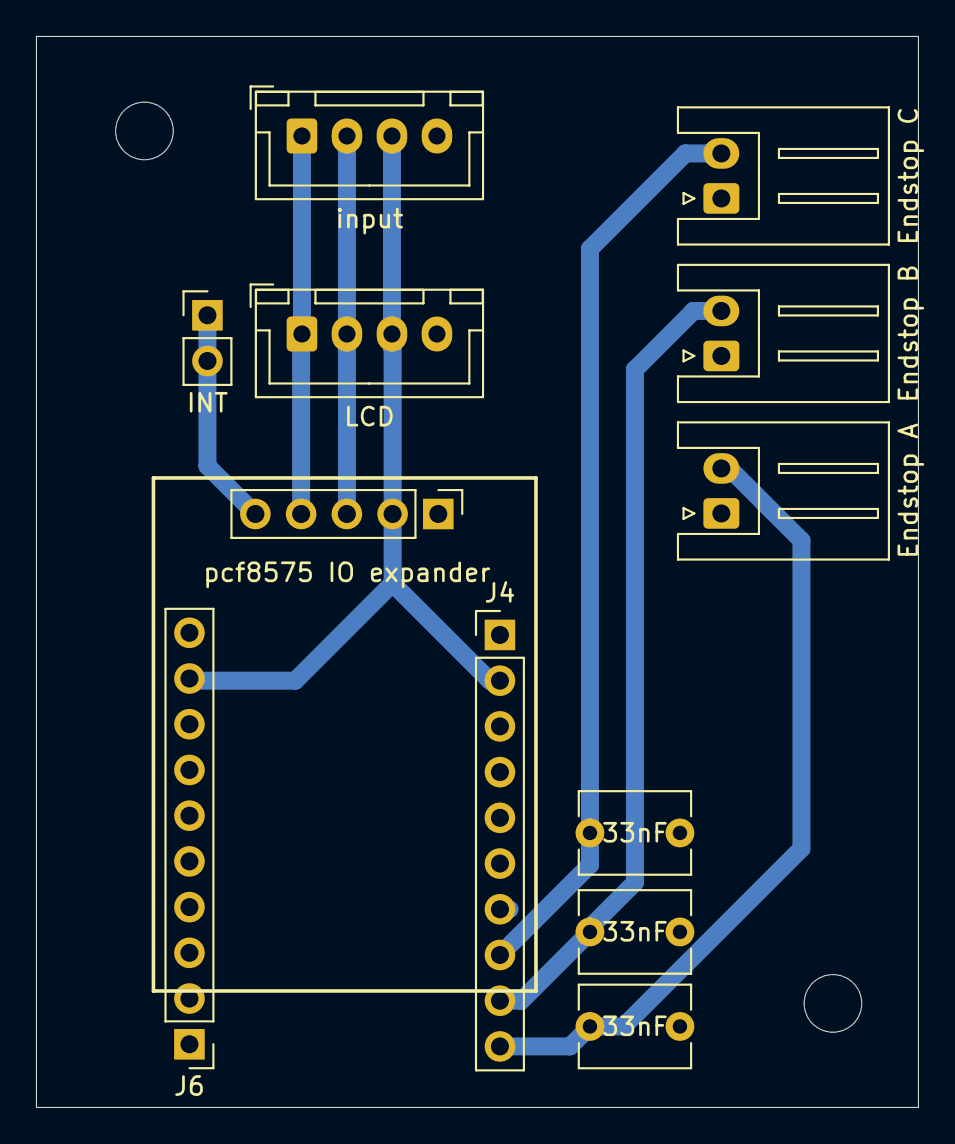
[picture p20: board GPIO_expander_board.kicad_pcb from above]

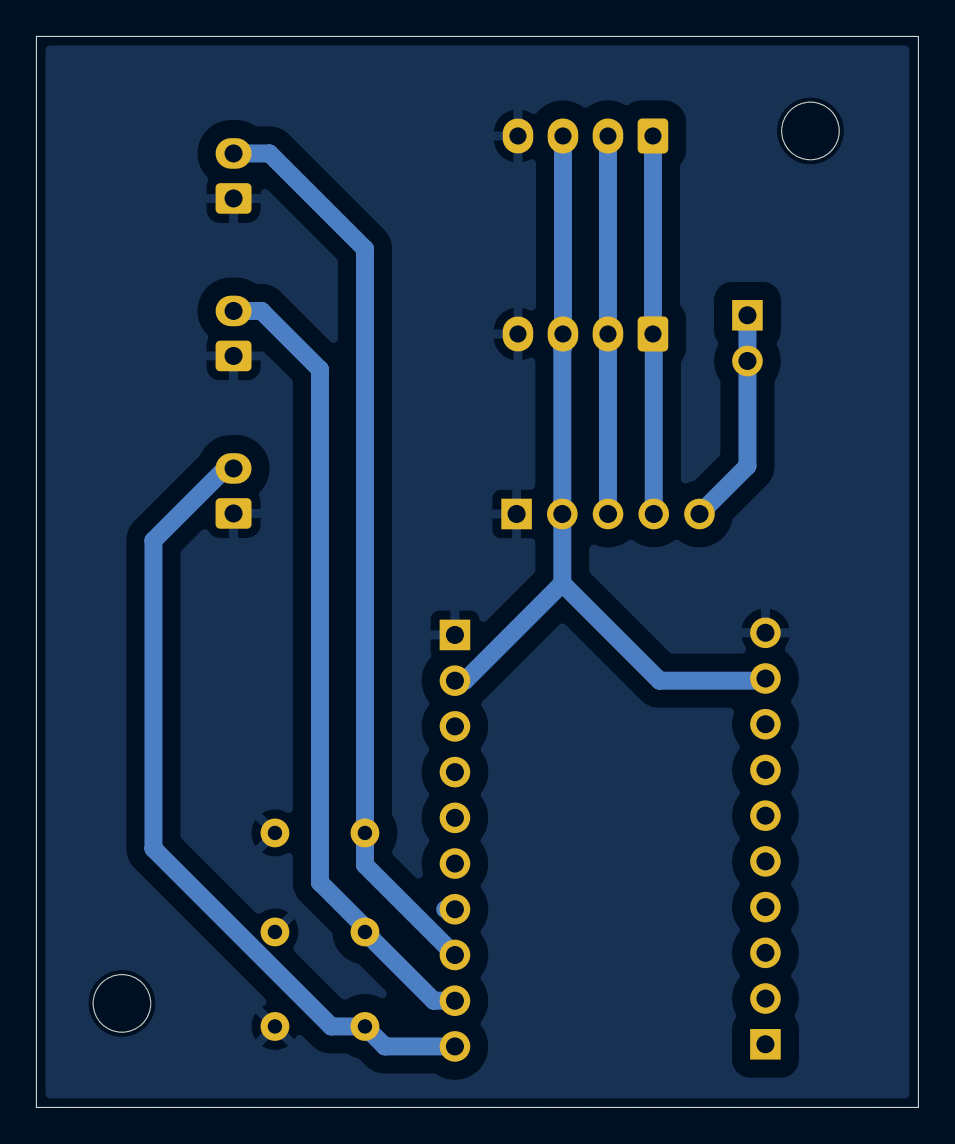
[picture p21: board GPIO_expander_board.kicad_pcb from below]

Board: 2 copper layers, 49.0 x 59.5 mm, 14 parts (2 on the bottom side), 8 nets.

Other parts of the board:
H4, H4#2: MountingHole; MountingHole_3.2mm_M3_DIN965

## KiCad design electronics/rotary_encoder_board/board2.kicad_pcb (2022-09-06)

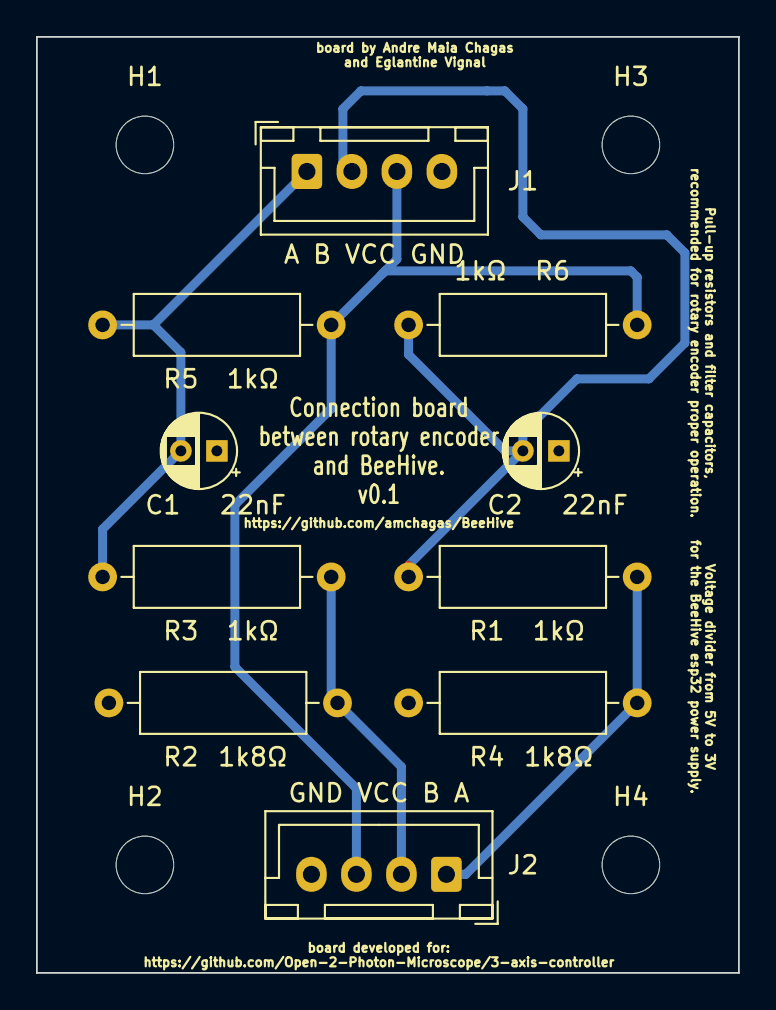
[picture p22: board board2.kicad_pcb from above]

Board: 2 copper layers, 39.0 x 52.0 mm, 14 parts (0 on the bottom side), 6 nets.

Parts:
C1, C2: 22nF; CP_Radial_D4.0mm_P2.00mm
H1, H2, H3, H4: MountingHole; MountingHole_3.2mm_M3_DIN965
J1: A B VCC GND; JST_XH_B4B-XH-A_1x04_P2.50mm_Vertical
J2: GND VCC B A; JST_XH_B4B-XH-A_1x04_P2.50mm_Vertical
R1, R3, R5, R6: 1kΩ; R_Axial_DIN0309_L9.0mm_D3.2mm_P12.70mm_Horizontal
R2, R4: 1k8Ω; R_Axial_DIN0309_L9.0mm_D3.2mm_P12.70mm_Horizontal

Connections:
+5V: J1.3, J2.3, R5.2, R6.2
GND: C1.1, C2.1, J1.4, J2.4, R2.1, R4.1
unnamed: C1.2, J1.1, R3.2, R5.1
unnamed: C2.2, J1.2, R1.2, R6.1
unnamed: J2.1, R1.1, R4.2
unnamed: J2.2, R2.2, R3.1

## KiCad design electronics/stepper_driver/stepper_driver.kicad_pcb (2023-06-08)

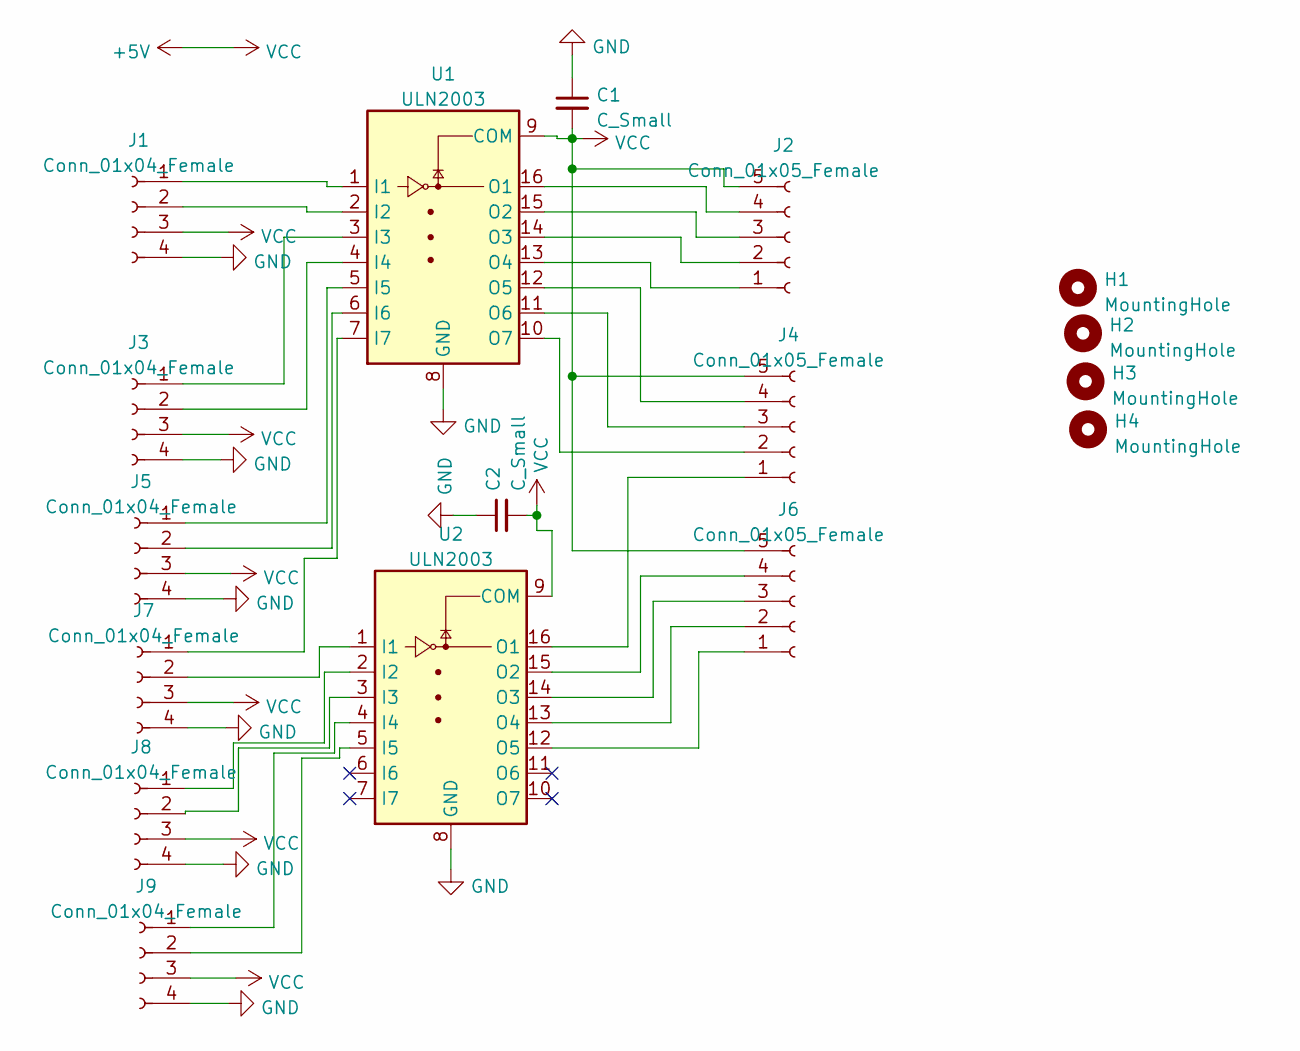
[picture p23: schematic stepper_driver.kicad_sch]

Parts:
C1, C2: C_Small; C_Disc_D6.0mm_W4.4mm_P5.00mm
H1, H2, H3, H4: MountingHole; MountingHole_3.2mm_M3
J1, J3, J5, J7, J8, J9: Conn_01x04_Female; JST_XH_S4B-XH-A-1_1x04_P2.50mm_Horizontal
J2, J4, J6: Conn_01x05_Female; JST_XH_S5B-XH-A_1x05_P2.50mm_Horizontal
U1, U2: ULN2003; DIP-16_W7.62mm_Socket_LongPads

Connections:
+5V: C1.2, C2.2, J1.3, J2.5, J3.3, J4.5, J5.3, J6.5, J7.3, J8.3, J9.3, U1.9 (COM), U2.9 (COM)
GND: C1.1, C2.1, J1.4, J3.4, J5.4, J7.4, J8.4, J9.4, U1.8 (GND), U2.8 (GND)
unnamed: J1.1, U1.1 (I1)
unnamed: J1.2, U1.2 (I2)
unnamed: J2.1, U1.13 (O4)
unnamed: J2.2, U1.14 (O3)
unnamed: J2.3, U1.15 (O2)
unnamed: J2.4, U1.16 (O1)
unnamed: J3.1, U1.3 (I3)
unnamed: J3.2, U1.4 (I4)
unnamed: J4.1, U2.16 (O1)
unnamed: J4.2, U1.10 (O7)
unnamed: J4.3, U1.11 (O6)
unnamed: J4.4, U1.12 (O5)
unnamed: J5.1, U1.5 (I5)
unnamed: J5.2, U1.6 (I6)
unnamed: J6.1, U2.12 (O5)
unnamed: J6.2, U2.13 (O4)
unnamed: J6.3, U2.14 (O3)
unnamed: J6.4, U2.15 (O2)
unnamed: J7.1, U1.7 (I7)
unnamed: J7.2, U2.1 (I1)
unnamed: J8.1, U2.2 (I2)
unnamed: J8.2, U2.3 (I3)
unnamed: J9.1, U2.4 (I4)
unnamed: J9.2, U2.5 (I5)

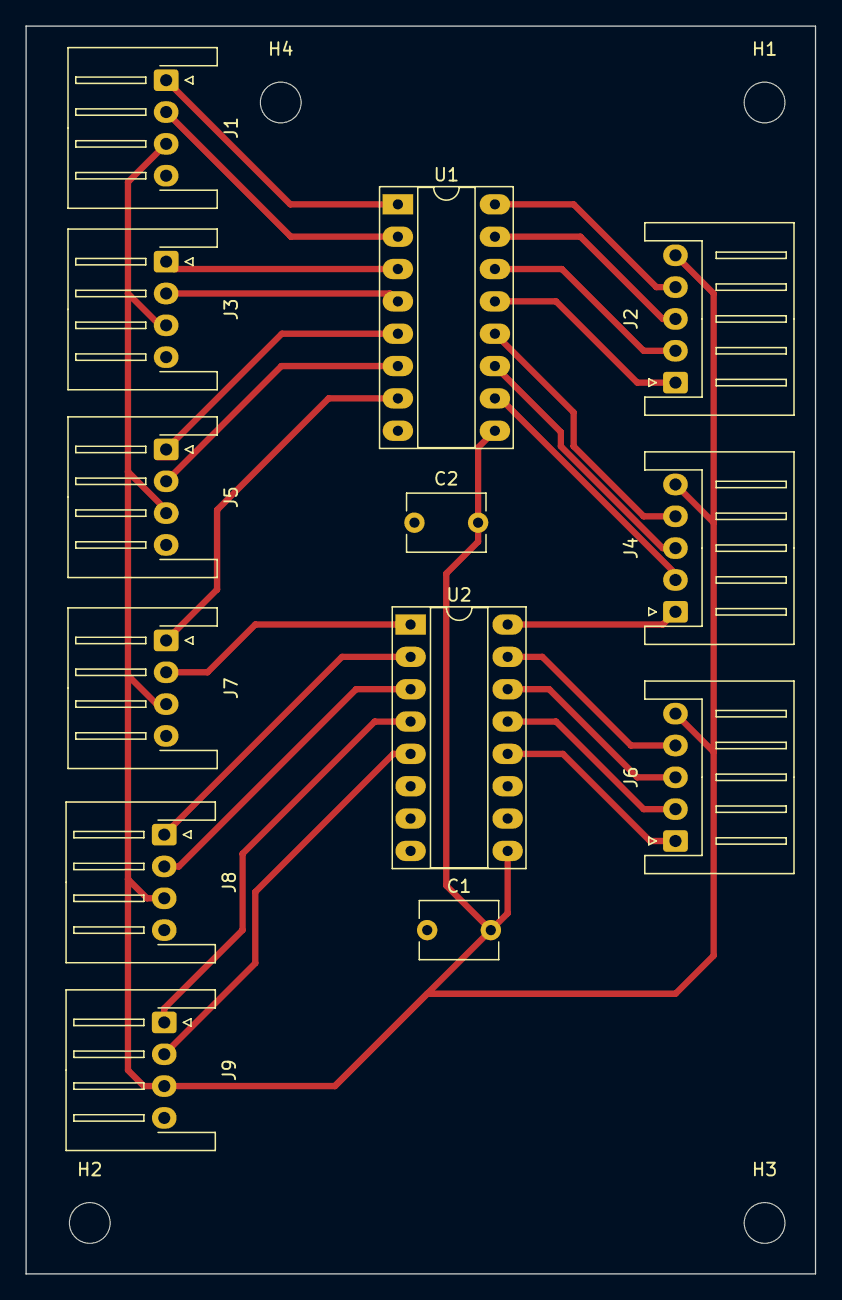
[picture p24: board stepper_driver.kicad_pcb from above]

Board: 2 copper layers, 62.0 x 98.0 mm, 17 parts (0 on the bottom side), 26 nets.

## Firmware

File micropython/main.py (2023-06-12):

import Stepper

from machine import Pin
'''
IN1 -->  16
IN2 -->  17
IN3 -->  5
IN4 -->  18
'''
s1 = Stepper.create(mode= "HALF_STEP",
                    pin1=Pin(16,Pin.OUT),
                    pin2=Pin(17,Pin.OUT),
                    pin3=Pin(5,Pin.OUT),
                    pin4=Pin(18,Pin.OUT),
                    delay=5)

s1.step(100)

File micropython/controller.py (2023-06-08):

from machine import Pin
from time import sleep
import Stepper

# PIN ASSIGNMENT FUNCTIONS
class controller():
    # function that assigns rotary encoders X, Y and Z channels (REC) to pins
    #        motor_a = self.pins_motor(26, 25, 14, 27)
#        motor_b = self.pins_motor(22, 23, 21, 19)
#        motor_c = self.pins_motor(1, 3, 9, 10)
    def __init__(self):
        self.xA,self.xB = self.pins_REC(15,2)
        self.yA,self.yB = self.pins_REC(16,17)
        self.zA,self.zB = self.pins_REC(5,18)
        
        self.motor_a = Stepper.create(mode= "HALF_STEP",
                    pin1=Pin(16,Pin.OUT),
                    pin2=Pin(17,Pin.OUT),
                    pin3=Pin(5,Pin.OUT),
                    pin4=Pin(18,Pin.OUT),
                    delay=5)
        self.motor_b = Stepper.create(mode= "HALF_STEP",
                    pin1=Pin(16,Pin.OUT),
                    pin2=Pin(17,Pin.OUT),
                    pin3=Pin(5,Pin.OUT),
                    pin4=Pin(18,Pin.OUT),
                    delay=5)
        self.motor_c = Stepper.create(mode= "HALF_STEP",
                    pin1=Pin(16,Pin.OUT),
                    pin2=Pin(17,Pin.OUT),
                    pin3=Pin(5,Pin.OUT),
                    pin4=Pin(18,Pin.OUT),
                    delay=5)        


    def pins_REC(self,pinA, pinB):
        outPinA = Pin(pinA, Pin.IN)
        outPinB = Pin(pinB, Pin.IN)
        self.outPinA = outPinA
        self.outPinB = outPinB
        return self.outPinA, self.outPinB

    # functions that assigns motor to pins
#    def pins_motor(self,pIN1, pIN2, pIN3, pIN4):
#        IN1 = Pin(pIN1, Pin.OUT)
#        IN2 = Pin(pIN2, Pin.OUT)
#        IN3 = Pin(pIN3, Pin.OUT)
#        IN4 = Pin(pIN4, Pin.OUT)
#        pins = [IN1, IN2, IN3, IN4]
#        self.pins = pins
#        return self.pins


# MOTOR FUNCTIONS

# function that assigns the step sequence
#    def step_sequence(self,n):
#        # clockwise sequence
#        if n > 0:
#            print('clockwise sequence')
#            sequence = [[1,0,0,0],[0,1,0,0],[0,0,1,0],[0,0,0,1]]  
#        # counterclockwise sequence
#        elif n < 0:
#            print('counterclockwise sequence')
#            sequence = [[0,0,0,1],[0,0,1,0],[0,1,0,0],[1,0,0,0]]
#        # freezing sequence
#        else:
#            sequence = [[0,0,0,0],[0,0,0,0],[0,0,0,0],[0,0,0,0]]
#            print('freezing sequence')
#        self.sequence = sequence
#        return self.sequence
        
# function that runs n steps on motor x
#    def run_step(self, n, motor_x):
#        sequence = step_sequence(n)
#        pins = motor_x
#        for k in range (0, abs(n)):
#            for step in sequence:
#                for i in range(len(pins)):
#                    pins[i].value(step[i])
#                    sleep(0.001)
#        return

# function that assigns motor rotations depending on translation axis
    def mov(self,vector):
        # clockwise
        print(vector)
        if vector[1]=="+":
            if vector[0] == "x":
                self.motor_a.step(-7)
                self.motor_b.step(7)
                #self.run_step(-7, motor_a)
                #self.run_step(7, motor_b)
            elif vector[0] == "y":
                self.motor_a.step(4)
                self.motor_b.step(4)
                self.motor_c.step(-8)
                
                #self.run_step(4, motor_a)
                #self.run_step(4, motor_b)
                #self.run_step(-8, motor_c)
            elif vector[0] == "z":
                self.motor_a.step(8)
                self.motor_b.step(8)
                self.motor_c.step(8)
                
                #self.run_step(8, motor_a)
                #self.run_step(8, motor_b)
                #self.run_step(8, motor_c)
        # counterclockwise
        elif vector[1]=="-":
            if vector[0] == "x":
                self.motor_a.step(7)
                self.motor_b.step(-7)
                #self.run_step(7, motor_a)
                #self.run_step(-7, motor_b)
            elif vector[0] == "y":
                self.motor_a.step(-4)
                self.motor_b.step(-4)
                self.motor_c.step(8)
                #self.run_step(-4, motor_a)
                #self.run_step(-4, motor_b)
                #self.run_step(8, motor_c)
            elif vector[0] == "z":
                self.motor_a.step(-8)
                self.motor_b.step(-8)
                self.motor_c.step(-8)
                #self.run_step(-8, motor_a)
                #self.run_step(-8, motor_b)
                #self.run_step(-8, motor_c)
        return


# ROTARY ENCODER FUNCTION

# function that translates REC signals into motor rotations
    def REC_translation(self,axis, outPinA, outPinB):
        oldA = outPinA.value() 
        oldB = outPinB.value()
        #print(oldB)
        sleep(0.005)

        vector = axis  
        A = outPinA.value()
        B = outPinB.value()    
        A_state = A-oldA
        B_state = B-oldB
       
        # channel A / clockwise
        if  A_state == 1 and B==0:
            vector += "+"
            self.mov(vector)
        # channel B / counterclockwise
        elif B_state == 1 and A==0:
            vector += "-"
            self.mov(vector)
        else:
            sleep(0.001)
     
        oldA = A
        oldB = B
        print('rec translation')
    
        return


    # PROGRAM
    def run(self):




        
            self.REC_translation("x",xA,xB)
            self.REC_translation("y",yA,yB)
            self.REC_translation("z",zA,zB)
            sleep(0.001)

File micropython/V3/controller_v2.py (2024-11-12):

import time
from rotary_irq_esp import RotaryIRQ
from machine import Pin
from screen import lcd


class controller():
    def __init__(self,
                 start_pin=Pin(36,Pin.IN),
                 stop_pin=Pin(39,Pin.IN),
                 display=lcd,
                 scale_factor=2,
                 step_size=0.5,
                 skip_init=False
                 ):
        self.start_pin = start_pin
        self.stop_pin = stop_pin
        self.display = display
        self.sf = scale_factor # how many steps per um
        self.step_size = step_size # how many steps per tick of encoder
        
        self.step_presets = [0.5, 1, 5, 10, 50, 100, 250]
        
        self.x_control = RotaryIRQ(pin_num_clk=34, 
                                    pin_num_dt=35, 
                                    min_val=0, 
                                    max_val=10000, 
                                    reverse=False, 
                                    range_mode=RotaryIRQ.RANGE_UNBOUNDED)
        
        self.y_control = RotaryIRQ(pin_num_clk=25, 
                                    pin_num_dt=26, 
                                    min_val=0, 
                                    max_val=10000, 
                                    reverse=False, 
                                    range_mode=RotaryIRQ.RANGE_UNBOUNDED)
        
        self.z_control = RotaryIRQ(pin_num_clk=27, 
                                    pin_num_dt=14, 
                                    min_val=0, 
                                    max_val=10000, 
                                    reverse=True, 
                                    range_mode=RotaryIRQ.RANGE_UNBOUNDED)
        
        #self.step_size = 0.5
        if skip_init == False:
            self.set_step_size()
        


    def set_step_size(self):
        self.display.clear()
        self.display.set_cursor(0,0)
        self.display.print("STEP SIZE: ")
        self.display.print(str(self.step_size))
        
        #self.display.blink()
        
        proposed_size = self.step_size
        
        old_val = self.x_control.value()
        new_val = old_val
        time.sleep_ms(500)
        self.x_control._incr = 1
        
        while self.start_pin.value()==0 and self.stop_pin.value()==0:
            new_val = self.x_control.value()
            if old_val != new_val:
                old_val = new_val
                proposed_size = self.step_presets[new_val % len(self.step_presets)]
                print('Step size: ', proposed_size)
                self.display.set_cursor(11,0)
                self.display.print('         ')
                self.display.set_cursor(11,0)
                self.display.print(str(proposed_size))
                time.sleep_ms(200)
        
        self.step_size = proposed_size
        self.x_control._incr = self.step_size*self.sf
        self.y_control._incr = self.step_size*self.sf
        self.z_control._incr = self.step_size*self.sf
        
        print('New size: ', proposed_size)
        self.x_control.set(value = 0)
        time.sleep_ms(300)
        self.display.clear()
    
    
    
    def live_read(self, cycles, ms=10, steps_taken=[0,0,0]):
        # only reset value if no step was taken prior
        if steps_taken[0] != 0:
            self.x_control.set(value = 0)
        if steps_taken[1] != 0:
            self.y_control.set(value = 0)
        if steps_taken[2] != 0:
            self.z_control.set(value = 0)
        
        old_pos = [self.x_control.value(),
                   self.y_control.value(),
                   self.z_control.value()]
        
        for i in range(cycles):
            new_pos = [self.x_control.value(),
                       self.y_control.value(),
                       self.z_control.value()]
            
            if new_pos != old_pos:
                old_pos = new_pos
                print('X,Y,Z:  ', new_pos)
            
            time.sleep_ms(ms)
        
        return new_pos

#c = controller()

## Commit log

2022-06-28 frame parts
    started to work on freecad to generate the frame for the manipulator
    [front-Part.stl, front-Part2.stl, front.FCStd]
2022-06-28 connection schematics
    [board.kicad_pcb]
2022-06-29 dump a bunch of new files
    [board.kicad_sch, front-Part.stl, front-Part2.stl, front.FCStd]
2022-08-17 v0.1 pcb
    [board.kicad_pcb, board.kicad_sch, board2.kicad_pcb, board2.kicad_sch]
2023-03-27 create drover board and update some code
    [bom.csv, designators.csv, positions.csv, stepper_driver.kicad_pcb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]
2023-04-21 fix major board failure
    [bom.csv, designators.csv, positions.csv, stepper_driver.kicad_pcb]
2023-06-08 update issue with board. clean code
    [bom.csv, designators.csv, positions.csv, stepper_driver.kicad_pcb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]
2023-12-05 update and create boards to streamline production
    [board2-B_Adhesive.gbr, board2-B_Courtyard.gbr, board2-B_Cu.gbr, board2-B_Fab.gbr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]
2023-12-13 moved ipynb files to legacy.
    All remaining files can be dragged and dropped into esp32 via thonny.
2024-06-07 update integrated board
    [bom.csv, designators.csv, integrated_board.kicad_pcb, integrated_board.kicad_sch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]
2024-06-26 introducing better code
    not yet finished.
    Faster + synchronous motor movement.
    More accurate/precise movement and readout** (currently in steps not uM)
    LCD works
    Improved rotary encoder reliability.
    Added start/stop buttons.
    [BILL OF MATERIALS OFDS.csv]
2024-07-25 finish revision of integrated pcb board, create production files
    [bom.csv, designators.csv, integrated_board.kicad_pcb, integrated_board.kicad_sch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]
2024-07-29 Updating README.md
    Updating micropython code
    V1 to be discontinued shortly
    V2 in still in testing
    Updating documentation for installation and assembly
2024-08-02 Optimise for new board
    - Inverted z control after new board seems to invert it.
    - Swapped pins talking to I2C to work with new board
2024-08-02 fix board bugs
    [bom.csv, designators.csv, integrated_board.kicad_pcb, integrated_board.kicad_sch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]
2024-08-07 enclosure design
    [enclosure.scad]
2024-08-11 Added modify step size
    also added feet to enclosure scad for TPU printing
    [enclosure.scad]
2024-09-04 added enclosure stl files
    [enclosure.stl, enclosure_feet.stl, enclosure_top.stl]
2024-09-05 added set_pins on boot
    prevents current from causing motor A to become hot before a stepper class is defined
2025-01-27 Redesign full enclosure
    A nice box to reduce exposed electronics of the project.
    [below.stl, enclosure.scad, enclosure.stl, enclosure_top.stl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]
2025-02-05 Expanding integrated board
    -Board now incorporates pcr8575 gpio expander
    -removed UART port
    [bom.csv, designators.csv, integrated_board-B_Cu.gbr, integrated_board-B_Mask.gbr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]
2025-02-13 Update PCB
    reintroduced push-switches as controlled by individual pins for better use of interrupts
    [integrated_board.kicad_pcb, integrated_board.kicad_sch]
2025-02-15 Updated PCB
    reintroduced voltage divider for switch 1 and 2 as pull up
    [integrated_board.kicad_pcb, integrated_board.kicad_sch]
2025-02-17 Introduced Endstops
    >Endstops class interrupts motor movement
    >re-addressed live movement
    >reorganised the micropython folder to be drag-and-drop friendly
2025-02-26 modular endstop upgrade board
    added board to include expander module and interface with endstops
    [GPIO_expander_board-B_Cu.gbr, GPIO_expander_board-Edge_Cuts.gbr, GPIO_expander_board-NPTH.drl, GPIO_expander_board-PTH.drl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]
2025-02-26 Updated endstop protocol
    [integrated_board.kicad_pcb, integrated_board.kicad_sch]
2025-02-27 Fixed enclosure clash
    previous back-slot prevented alignment of screws by clashing with the JTS XH5 connector for motor A
    [enclosure.scad, enclosure.stl]
2025-02-27 Updated controls
    -Updated boot to load and run on startup
    - Both buttons pressed will instantly stop all motors
    - Backlash default value set to 100
2025-02-28 Updated integrated PCB
    - fixed footprint for pcf8575
    - updated footprint for rotary encoder connectors for ease of use
    [integrated_board.kicad_pcb, integrated_board.kicad_sch]
2025-02-28 update enclosure
    - updated design to avoid clashing footprints in the board / enclosure
    - updated gerbers
    -added some illustration images
    -updated README
    [enclosure.scad, enclosure.stl, integrated_board-B_Cu.gbr, integrated_board-B_Mask.gbr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]
2025-02-28 Documentation updated
    [integrated_board-B_Cu.gbr, integrated_board-B_Mask.gbr, integrated_board-B_Paste.gbr, integrated_board-B_Silkscreen.gbr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]
2025-03-03 Updated BOM
    [BILL OF MATERIALS OFDS.csv, BOM.csv, BOM.xlsx, integrated_board.csv]
2025-03-04 Updated documentation
    [BOM.xlsx]
2025-05-29 Added BNC connectors to board
    Intended as receivers of trigger signal for Z-stack
    [integrated_board.kicad_pcb, integrated_board.kicad_sch]
2025-09-27 Ergonomic controller design
    [3-axis-controller.scad, 3-axis-controller.stl, enclosure.scad, wheel.scad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]
2025-09-27 Added set_backlash() to stage
2025-09-30 enclosure draft optimisation
    [3-axis-controller.scad, wheel.scad]

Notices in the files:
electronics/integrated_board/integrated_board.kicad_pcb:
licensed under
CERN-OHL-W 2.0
